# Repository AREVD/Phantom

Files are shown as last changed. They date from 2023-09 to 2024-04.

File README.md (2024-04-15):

# Camera Sensor-Embedded Phantom Model for External Ventricular Drain
This repository contains the developmental artifacts for the custom phantom skull model used in the paper _"Did I Do Well? Personalized Assessment of Trainees' Performance in Augmented Reality-assisted Neurosurgical Training"_, presented at **the 5th Annual Workshop on 3D Content Creation for Simulated Training in eXtended Reality, co-located with IEEE VR, 2024** by [Sarah Eom](https://sites.duke.edu/sangjuneom/), [Tiffany Ma](https://sites.duke.edu/tiffanyma/), [Tianyi Hu](http://hutianyi.tech/), Neha Vutakuri, Joshua Jackson, and [Maria Gorlatova](https://maria.gorlatova.com/). The repository includes all of the relevant code and assets necessary for the implementation of real-time distance calculation.

# Outline
1. [Overview](https://github.com/AREVD/Phantom/blob/main/README.md#overview)
2. [Hardware Setup](https://github.com/AREVD/Phantom/blob/main/README.md#hardware-setup)
3. [Software Setup](https://github.com/AREVD/Phantom/blob/main/README.md#hardware-setup)
4. [Quick Start](https://github.com/AREVD/Phantom/blob/main/README.md#quick-start)

# Overview

The integration of Augmented Reality (AR) in neurosurgery provides guidance to surgeons through the visualization of patient-specific anatomy by enhancing their field of view. Our lab has developed an AR-assisted training system for a neurosurgical procedure, the placement of an external ventricular drain (EVD), using marker-based tracking of a phantom model and surgical tool. EVD is performed in order to alleviate pressure built in the ventricular system of the brain due to excess cerebrospinal fluid (CSF). In this procedure, surgeons drill a small hole in the skull through which they place a catheter that drains the CSF to an external closed system.

Our AR system provides real-time feedback to the user, who performs a catheter insertion through a pre-drilled hole in the phantom skull model. The guidance includes a distance-to-target value as an evaluation of the user's accuracy. This value is measured from the tip of the catheter to the location of the target point, the foramen of Monro. The distance is computed in real-time using a stereo-camera setup within the phantom model. The rest of this README details both the hardware and software implementation of this stereo-camera setup.

# Hardware Setup

## Materials

### Raspberry Pi 
1. [Raspberry Pi 4 Model B](https://www.raspberrypi.com/products/raspberry-pi-4-model-b/)
2. (2x) [Arducam Fisheye Camera for Raspberry Pi](https://www.arducam.com/product/arducam-ultra-wide-angle-fisheye-5mp-ov5647-camera-for-raspberry-pi/)
3. [Arducam Multi Camera Adapter for Raspberry Pi](https://www.arducam.com/product/multi-camera-v2-1-adapter-raspberry-pi/)
4. (2x) [A1 FFCs 60cm Raspberry Pi Camera Extension Cable](https://a.co/d/9ydk6Bi)

### Gelatin Mold
1. [SimbaLux Acrylic Sheets](https://a.co/d/h83qMPt)
2. [CHANZON White LED Diode Lights](https://a.co/d/ftPlEu8)
3. [PandaHall Metal Beads](https://a.co/d/ffelK5M)
4. [Custom Collagen SuperClear Gelatin](https://customcollagenshop.com/products/superclear-gelatin)

### Additional Tools and Materials
1. Hot glue and hot glue gun
2. Nuts and bolts for securing cameras onto camera mounts
3. Electrical tape for securing camera mounts to gelatin mold
4. (2x) Female to female DuPont wires (~50cm)
5. Laser cutter or precision knife
6. [CODMAN BACTISEAL EVD Catheter Set](https://www.integralife.com/codman-bactiseal-evd-catheter-set/product/neurocritical-care-evd-catheters-bactiseal-anti-microbial-catheter-codman-bactiseal-evd-catheter-set)
7. Colored polish/paint or silicone dye

All 3D models were printed using PLA filament and Ultimaker 3 printers. Black filament was used to print the gelatin mold and camera mounts to create a high-contrast environment for the cameras, and light grey filament was used to print the phantom skull to present a non-distracting visual experience to the user.

## Camera Hardware Setup

<p align="center">
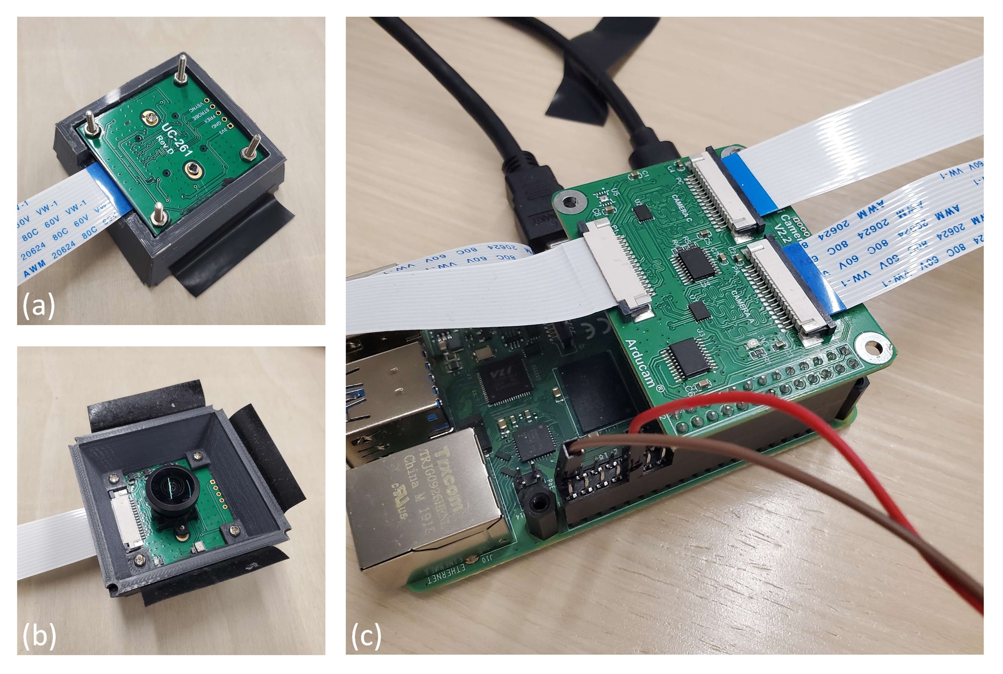
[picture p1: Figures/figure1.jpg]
  
</p>
<p align="center">
Figure 1. Camera hardware setup steps.
	</p>
 
Required 3D print: [Camera_mounts.stl](https://github.com/AREVD/Phantom/blob/main/3D%20Models/Camera_mounts.stl)

1. Replace cameras' native cables with the 60cm extension cables.
2. Secure cameras to camera mounts using nuts and bolts on the four corners of each camera (Fig. 1a, 1b).
3. Connect cameras to the multi camera adapter's A and C ports using the extension cables (Fig. 1c).
4. Mount the adapter to pins 1-26 of the Raspberry Pi. Secure with nuts and bolts if desired.
5. Connect the adapter's camera cable to the Raspberry Pi.

## Gelatin Mold Setup

<p align="center">
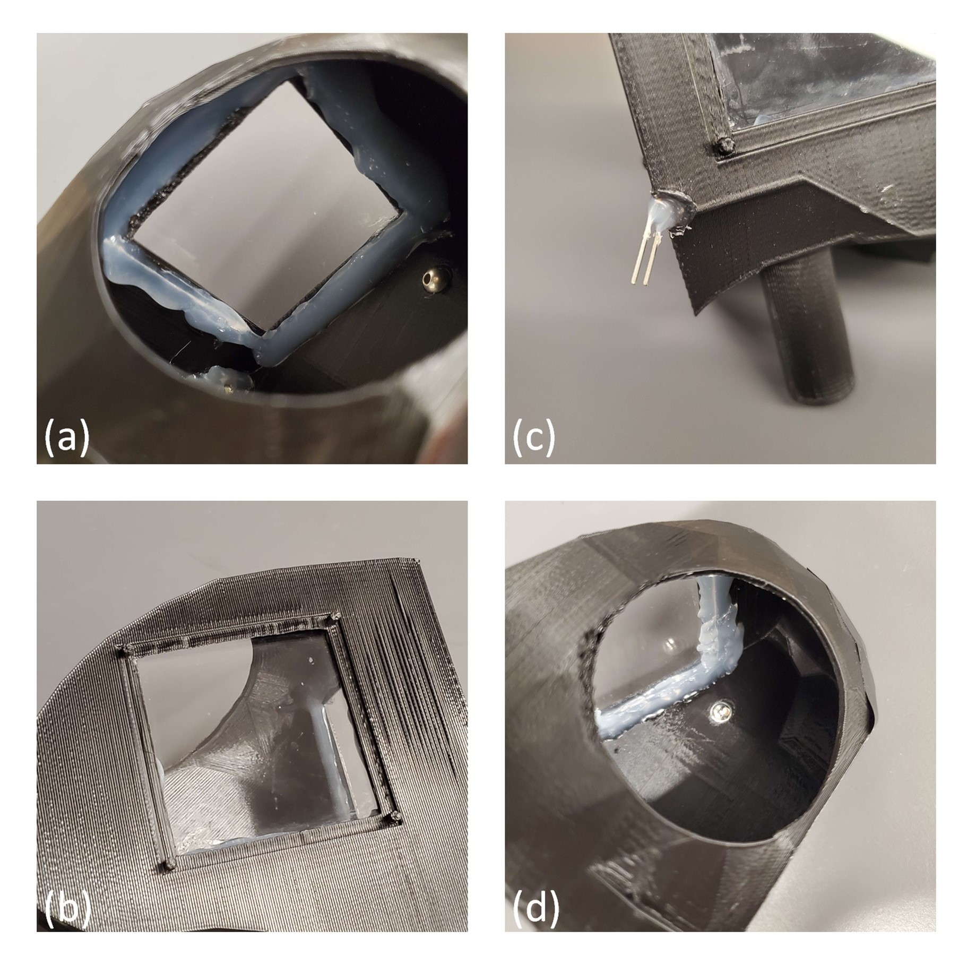
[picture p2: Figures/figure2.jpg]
  
</p>
<p align="center">
Figure 2. Gelatin mold setup steps.
	</p>

Required 3D print: [Gelatin_mold.stl](https://github.com/AREVD/Phantom/tree/main/3D%20Models/Gelatin_mold.stl)

1. Cut acrylic sheets into 2-inch squares. Two squares are needed per mold.
2. Secure squares from the inside of the gelatin mold using hot glue along all edges of the squares (Fig. 2a, 2b).
3. Secure LED diode light to the bottom corner between the two camera windows using hot glue (Fig. 2c).
4. Secure 6mm metal bead to the spherical indentation within the mold (Fig. 2d).
5. Ensure the mold is water-tight by filling it with water; if not, add hot glue as necessary.
6. Connect the LED diode light to pins 32 (GPIO 12) and 34 (Ground) using DuPont wires (Fig. 1c). 

## Gelatin Mixture Instructions

<p align="center">
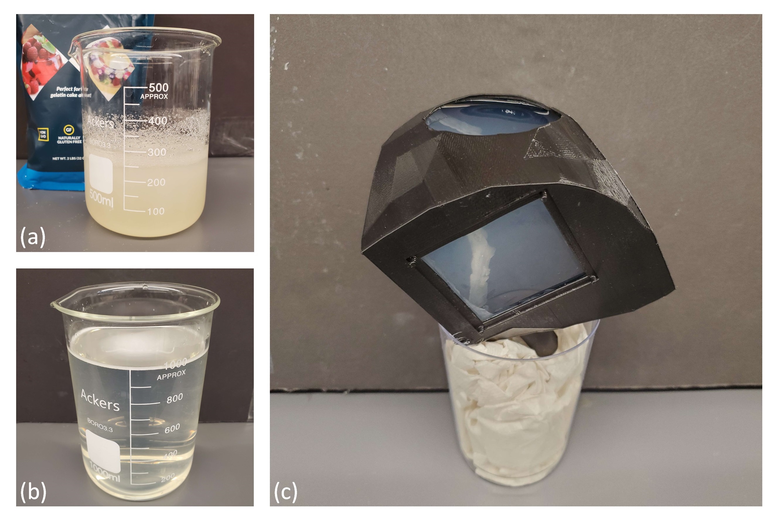
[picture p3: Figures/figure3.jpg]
  
</p>
<p align="center">
Figure 3. Gelatin mixture setup steps.
	</p>

The following steps yield three molds' worth of gelatin mixture.

1. Weigh out 20g of gelatin and combine with 250ml of cold water. Mix until clumping is no longer visualized (Fig. 3a). Let sit for 10-15 minutes.
2. Heat 700ml of water until steam is visualized. Closely monitor and do not allow to boil. A microwave is sufficient for heating.
3. Combine the gelatin mixture with the larger volume of water. Mix thoroughly until mixture is clear (Fig. 3b).
4. Cool mixture to room temperature. This can be accelerated by refrigerating the mixture. *Note: Closely monitor to prevent excessive cooling, which would cause the gelatin to coagulate prematurely.*
5. Disconnect the gelatin molds' LED diode light from the DuPont wires.
6. Suspend the molds in a cup or other container using paper towels or other supports such that the circular opening faces upwards and is parallel to the ground.
7. Fill the molds with the mixture up to the opening (Fig. 3c).
8. Refrigerate for at least 1 hour.

## Final Hardware Setup

<p align="center">
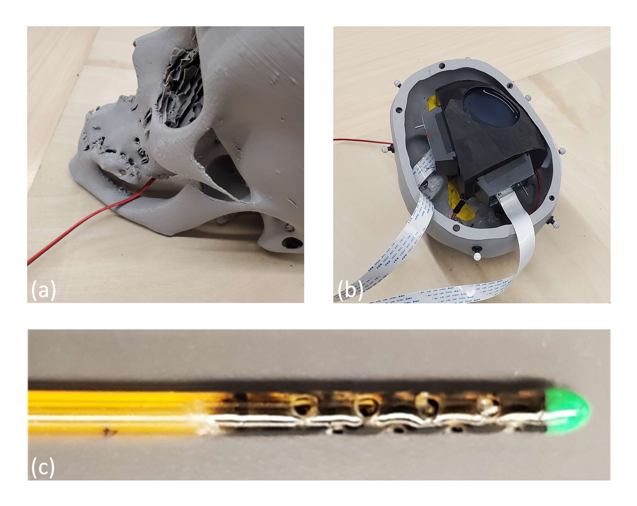
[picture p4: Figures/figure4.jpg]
  
</p>
<p align="center">
Figure 4. Final hardware setup steps.
	</p>

Required 3D prints: [Top_skull_pegs.stl](https://github.com/AREVD/Phantom/tree/main/3D%20Models/Top_skull_pegs.stl), [Bottom_skull_pegs.stl](https://github.com/AREVD/Phantom/tree/main/3D%20Models/Bottom_skull_pegs.stl)

1. Thread the DuPont wires through the holes in the bottom of the phantom into the inside of the phantom (Fig. 4a).
2. Connect the DuPont wires to the LED diode light of the gelatin mold (Fig. 4b).
3. Secure the camera mounts onto the gelatin mold using electrical tape. Position A at the back of the phantom and C on the right side of the phantom.
4. Insert the mold into the peg in the center of the phantom.
5. Close the phantom by connecting the top of the skull to the bottom of the skull. Secure with tape if necessary.
6. Color the tip of the catheter using polish, paint, or silicone dye in a 2mm region (Fig. 4c). Our development uses a green color, but a different bright color that looks distinct from the rest of the environment (mold color, catheter color) may be used, although some colors may be suboptimal.

# Software Setup

*Note: Our development uses a Raspberry Pi 4 Model B running Raspbian OS. The steps below may not work as expected on different operating systems.

1. Install the following packages using a Raspberry Pi terminal.

```
sudo apt install python3-opencv
sudo apt-get install python3-numpy
sudo apt-get install python3-picamera2
sudo apt-get install python3-scipy
sudo apt-get install python3-matplotlib
pip install keyboard
```

2. Disable the legacy camera option in Raspberry Pi configuration settings. If this option cannot be found in the settings menu, the configuration menu can be accessed by typing `raspi-config` into a terminal. A reboot will be required.

*Note: For troubleshooting regarding the multi camera adapter, please refer to the [Arducam documentation of the product.](https://docs.arducam.com/Raspberry-Pi-Camera/Multi-Camera-CamArray/Multi-Camera-CamArray/#arducam-multi-camera-adapter-board)*

## Quick Start

<p align="center">
  
</p>
<p align="center">
Figure 5. Quick start application.
	</p>

We provide a straightforward script, [AR.py](https://github.com/AREVD/Phantom/blob/main/Quick%20Start/AR.py), 
for real-time distance calculation, as well as a video feed from both cameras, utilizing camera calibration 
optimized for our experimental setup (Fig. 5). The images and code used for calibration can be found in [this folder.](https://github.com/AREVD/Phantom/tree/main/Fisheye%20Calibration%20Core) The output files of stereo.py are used to perform stereo camera calibration when running AR.py.

*Note: Some calibration images were post-processed to improve image clarity for the checkerboard recognition stage of camera calibration.*

### Notes

+ The location of the foramen of Monro is specified in the `triangulate` function as the variables `pointA` and `pointB`. These values can be adjusted if necessary.
+ The tip of the catheter is colored green in our development, and the code reflects this in lines 153-158 (see below). 
  These RGB 
  value thresholds are responsible for identifying the 2D location of the tip of the catheter in each camera view by identifying green pixels and finding the average of the x and y coordinates of the pixels. These thresholds can be adjusted to handle differences in lighting conditions and/or different color choices for the catheter tip.
```
if buf is not None:
    if item == "A":
        lower = [14, 110, 0]  # color green boundaries
        upper = [70, 255, 156]
    elif item == "C":
        lower = [14, 140, 0]  # color green boundaries
        upper = [70, 255, 156]
```
+ Manual offsets in line 190 can be adjusted to accommodate differences in observed distance values, which may result 
  from variations between individual cameras.
```
c = str('%.2f' % (abs(6.6 * round(triangulate(mtxA, mtxB, R, T, ptA, ptC), 2) - 1.7)))
```
+ The brightness level is set using pulse width modulation (PWM), as full brightness can often make the 
  identification of the catheter tip color difficult due to over-exposure. This results in visible flickering of the 
  LED, which is expected. The brightness level is set at 25% in lines 103-104 (see below), and can be adjusted as 
  necessary.
```
p = gp.PWM(32,25)
p.start(25)
```
+ We set up a wireless network communication system using multithreading to send these distance results in real time to 
  our AR 
  headset, the Microsoft 
  HoloLens 2. This implementation was omitted from the Quick Start script for simplicity as it is highly tailored to 
  our 
  experimental setup.

# Associated Demo
The associated demo, _"Did You Do Well? Real-Time Personalized Feedback on Catheter Placement in Augmented Reality-assisted Neurosurgical Training"_, presents an AR-assisted neurosurgical training tool that provides real-time personalized feedback based on trainees' manipulation of the surgical environment and eye gaze patterns. The video of this demo can be found on [YouTube](https://youtu.be/AKNKKrCvapI). 

# Citation
Please cite the following paper in your publications if this code helps your research.
```
@inproceedings{Eom24ARNeuro,
  title={Did I Do Well? Personalized Assessment of Trainees' Performance in Augmented Reality-assisted Neurosurgical Training},
  author={Eom, Sangjun and Ma, Tiffany and Hu, Tianyi and Vutakuri, Neha and Jackson, Joshua and Gorlatova, Maria},
  booktitle={Proc. IEEE Conference on Virtual Reality and 3D User Interfaces Abstracts and Workshops (VRW)},
  year={2024},
  organization={IEEE}
}
```
# Acknowledgments
The contributors of the code are [Tiffany Ma](https://sites.duke.edu/tiffanyma/), [Sarah Eom](https://sites.duke.edu/sangjuneom/), and [Maria Gorlatova](https://maria.gorlatova.com/). For questions on this repository or the related paper, please contact Sangjun (Sarah) Eom at sangjun.eom [AT] duke [DOT] edu.

This work was supported in part by NSF grants CNS-2112562 and CNS-1908051, NSF CAREER Award IIS-2046072, and by a Thomas Lord Educational Innovation Grant.

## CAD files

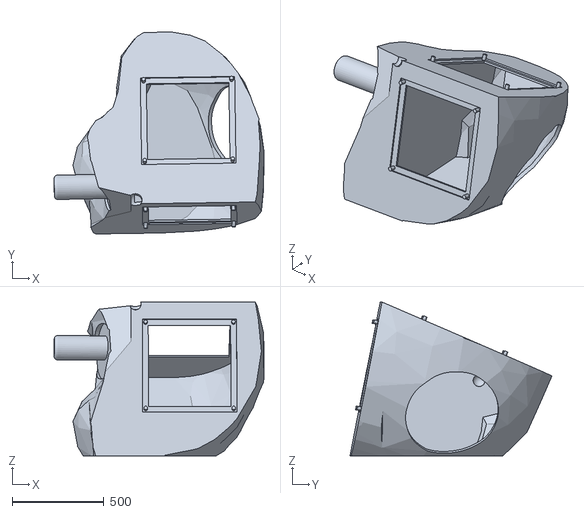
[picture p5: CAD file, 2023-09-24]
3D Models/Gelatin_mold.stl
1145.7 x 1101.9 x 839.9

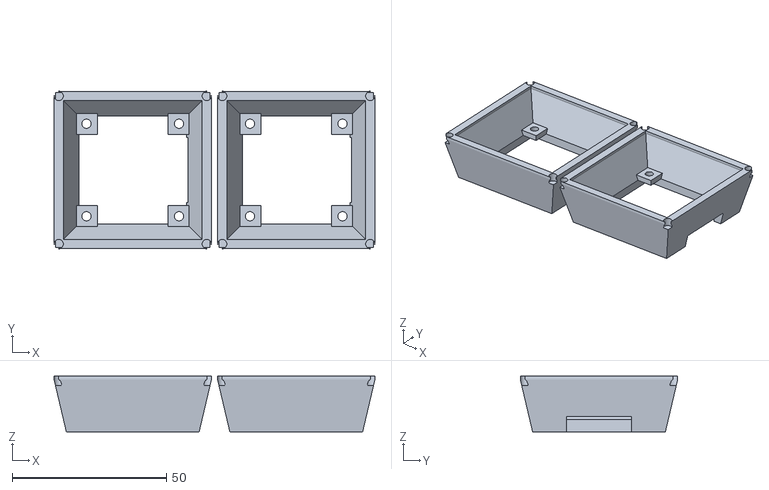
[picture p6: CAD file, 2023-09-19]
3D Models/Camera_mounts.stl
104.1 x 51.1 x 18.0

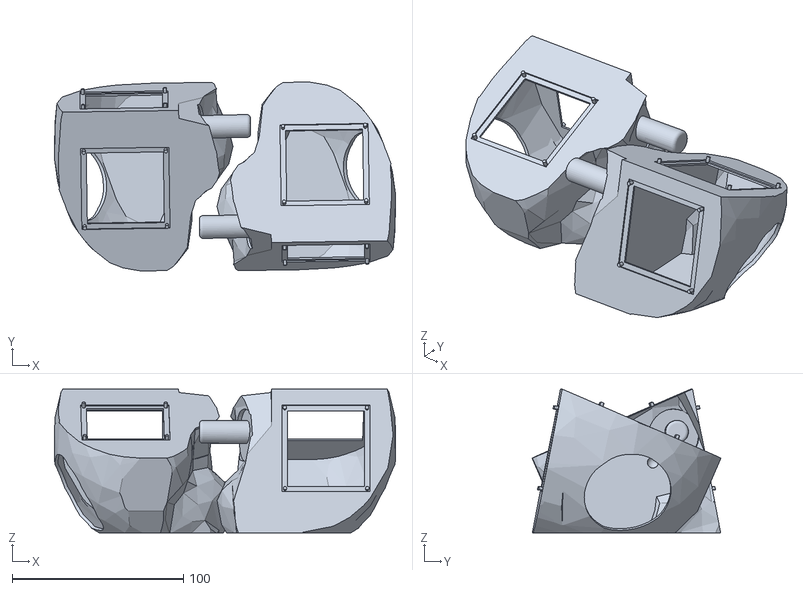
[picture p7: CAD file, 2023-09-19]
3D Models/Gelatin_mold_2_copies.stl
199.1 x 110.4 x 84.0

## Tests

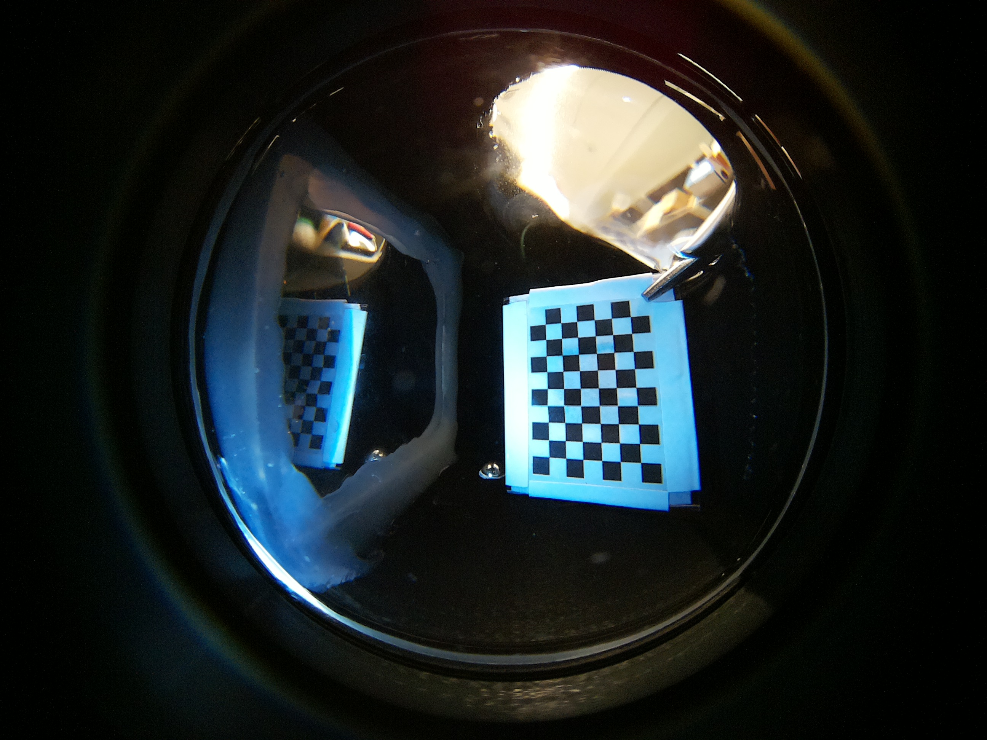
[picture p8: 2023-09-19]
Fisheye Calibration Core/A/capture_A43.jpg

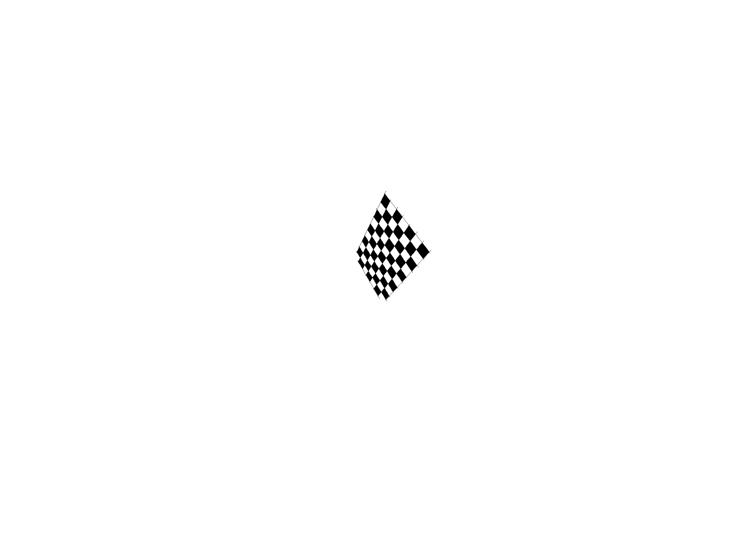
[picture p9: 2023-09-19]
Fisheye Calibration Core/A/capture_A59.jpg

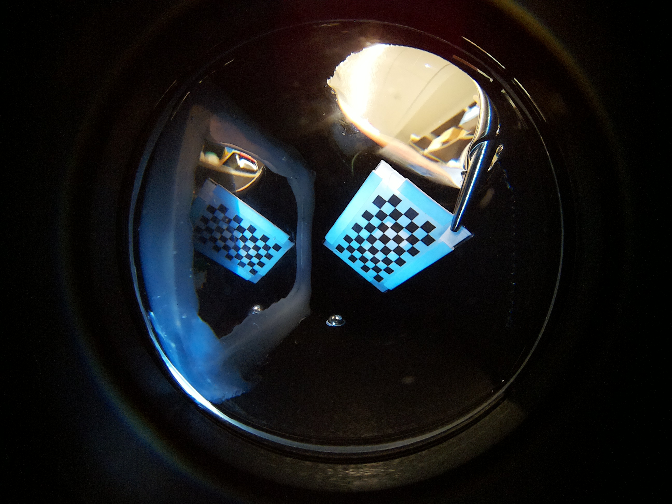
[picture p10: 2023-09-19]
Fisheye Calibration Core/A/capture_A17.jpg

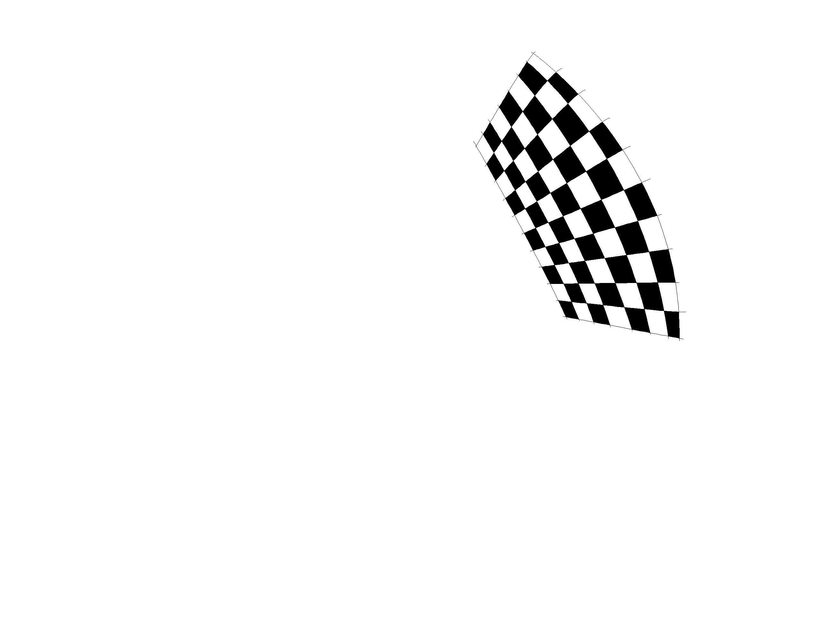
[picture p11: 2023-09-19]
Fisheye Calibration Core/A/capture_A61.jpg

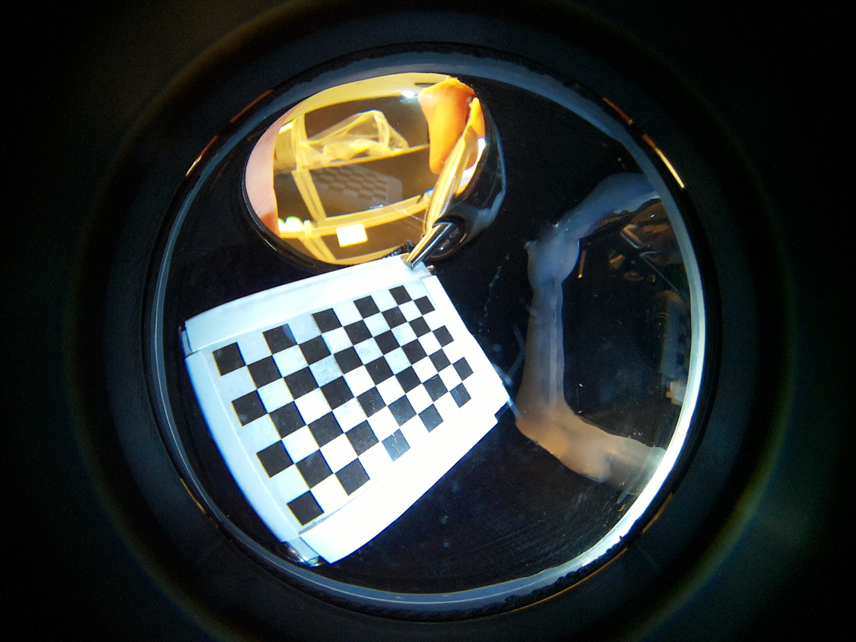
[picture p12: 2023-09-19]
Fisheye Calibration Core/B/capture_B63.jpg

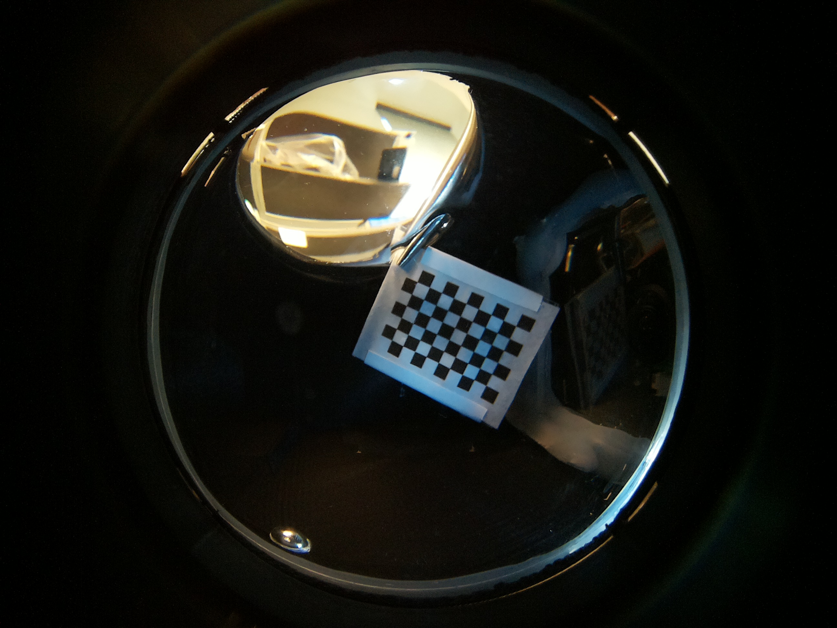
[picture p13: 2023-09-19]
Fisheye Calibration Core/B/capture_B6.jpg

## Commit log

2023-09-19 Added 3D Models and Fisheye Calibration Core
    [Camera_mounts.stl, Gelatin_mold.stl, Gelatin_mold_2_copies.stl]
2023-09-24 Simplified AR.py and README
    [Gelatin_mold.stl]
